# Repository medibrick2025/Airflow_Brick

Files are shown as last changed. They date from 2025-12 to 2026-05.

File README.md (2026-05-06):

# Airflow / Spiro Brick

The Spiro Brick interfaces with the [Sensirion SFM3300-D](https://sensirion.com/products/catalog/SFM3300-D) airflow sensor. It also enables airway pressure measurement using Amphenol differential pressure sensor such as [ELVH-family](https://allsensors.com/en/product-listing?family=elvh) with I2C 3.3V or 5V interface.

- [Datasheet SFM3300](./datasheets/Sensirion_Datasheet_SFM3300-AW_SFM3300-D.pdf)
- [Datasheet ELVH Family](./datasheets/DS-0376.pdf)

Example differential pressure sensor with I2C and 5V interface: ELVH-M160D-HRRD-C-N2A5 for 1/16 ID 1/8 OD tubing.

## Documentation

- [Education Background](./spirometer%20educational%20background/)
- [Assembly Instructions](./Spirometer%20Mechanical%20Design%20And%20Mechanical%20Assembly/)
- [Software / Firmware](./Spirometer%20Software/)

## SFM3300

- [Cleaning](./datasheets/Sensirion_GF_AN_SFM-21_Cleaning_Methods_D1.pdf)
- [Eval Kit](./datasheets/Sensirion_GF_AN_SFM-22_ClipOn_CapCable_Evaluation_Kit_D1_1.pdf)
- [Arduino Driver Sensirion](https://github.com/Sensirion/arduino-i2c-sfm3000) with [Sensirion Arduino Core](https://github.com/Sensirion/arduino-core)
- [Arduino Driver Alternative](https://github.com/MyElectrons/sfm3300-arduino)
 
## Spiro Brick PCB Design

The following files were created for this project using KiCad.

<a href="./KiCad/Altekreeti/Spiro_Brick.svg" target="_blank">
  Schematics
</a>

[View schematics as PDF](./KiCad/Altekreeti/Spiro_Brick.pdf)

<a href="./KiCad/Altekreeti/Spiro_Brick_Front.png" target="_blank"> 
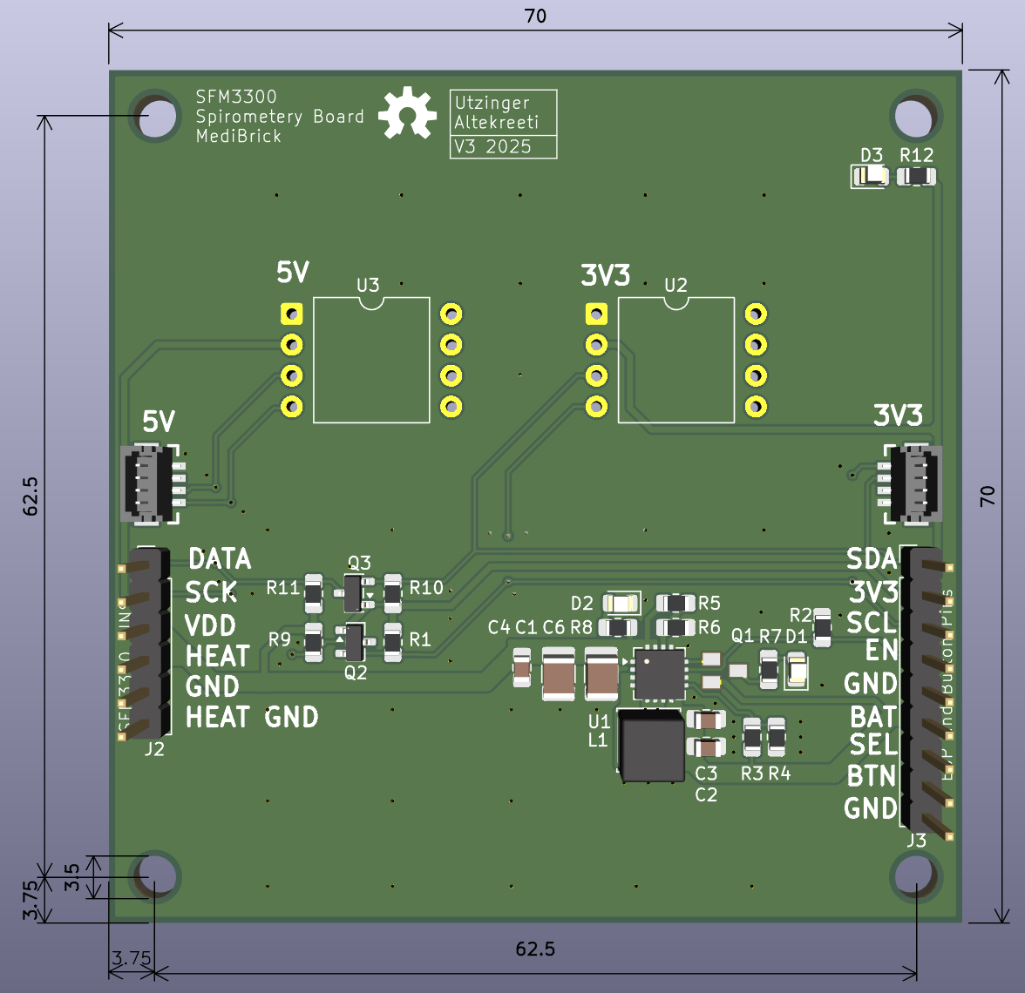
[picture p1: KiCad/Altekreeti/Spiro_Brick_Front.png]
  
</a>

<a href="./KiCad/Altekreeti/Spiro_Brick_Back.png" target="_blank">
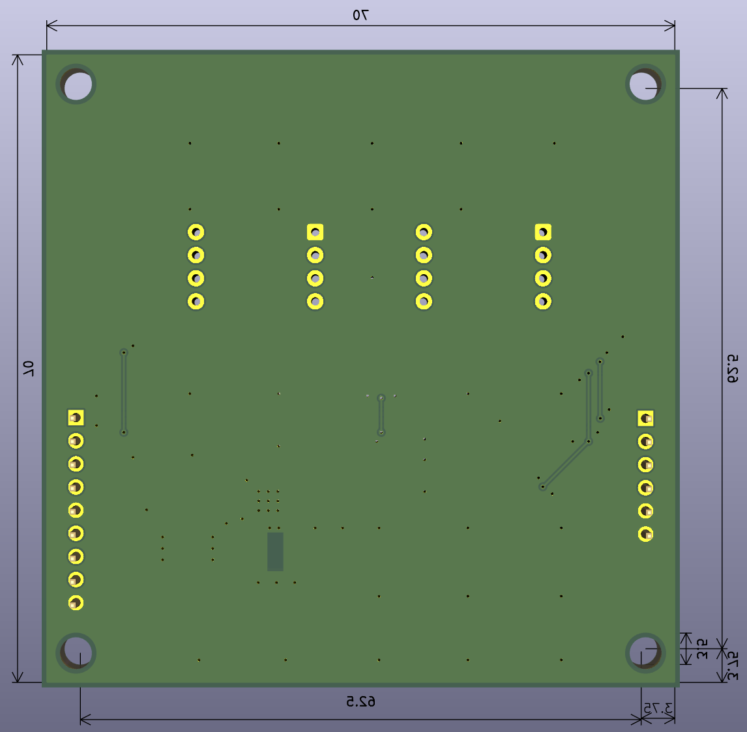
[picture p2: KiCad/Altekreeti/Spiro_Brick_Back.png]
  
</a>

## LiPo to 5V Power Boost

- [Ti TPS61090 Eval](./reference_designs/TPS61090_sbvu003.pdf)
- [Adafruit](https://learn.adafruit.com/adafruit-powerboost-500-plus-charger/downloads)

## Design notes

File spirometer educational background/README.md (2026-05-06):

**Introduction to Spirometry and Lung Volumes**

Spirometry is a fundamental respiratory test used to assess lung function by measuring the volume and flow of air during inhalation and exhalation. The test provides insights into a patient's breathing patterns and can be used to detect and monitor respiratory diseases. The Figure below shows the key lung volumes measures which includes:

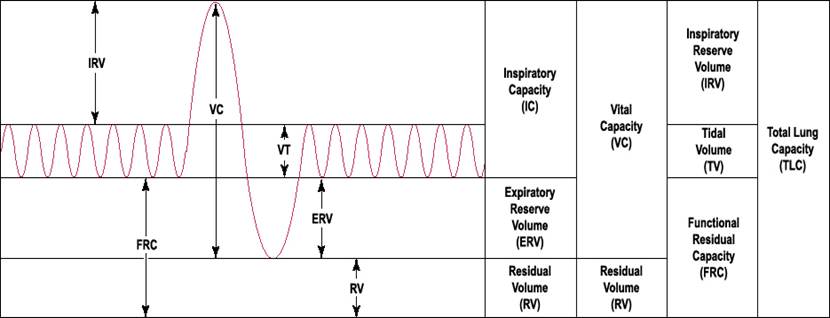
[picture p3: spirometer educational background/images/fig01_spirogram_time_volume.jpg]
Figure 1. Example spirogram showing lung volume as a function of time


[source](https://histology.oit.duke.edu/MBS/Videos/Phys/Phys%205.2%20Resp%20Lung%20Volumes/Phys%205.2%20Resp%20Lung%20Volumes.pdf)

- **Tidal Volume (TV):** The amount of air inhaled or exhaled during normal, resting breathing (typically 400–600 mL).
- **Inspiratory Reserve Volume (IRV):** Additional air that can be forcibly inhaled after a normal inhalation (~ above 1700 mL).
- **Expiratory Reserve Volume (ERV):** Additional air that can be forcibly exhaled after a normal exhalation (~800–1200 mL).
- **Residual Volume (RV):** Air remaining in the lungs after maximal exhalation (~1200 mL); not measurable by spirometry.
- **Inspiratory Capacity (IC):** Maximum air that can be inhaled after a normal exhalation; **IC = TV + IRV.**
- **Functional Residual Capacity (FRC):** Volume of air in lungs after a normal exhalation; **FRC = ERV + RV**.
- **Vital Capacity (VC):** Maximum amount of air that can be exhaled after a maximal inhalation; **VC = IRV + TV + ERV**.
- **Total Lung Capacity (TLC):** Total volume the lungs can hold; **TLC = VC + RV.**
- **Forced Vital Capacity (FVC):** The total amount of air exhaled during a forced breath (~3000–5000 mL).
- **FEV₁%:** The percentage of the FVC exhaled in the first second; this value helps assess obstruction ( +%90).
- **FEF₂₅–₇₅:** The average flow rate during the middle portion of a forced exhalation (4.5 L/s).

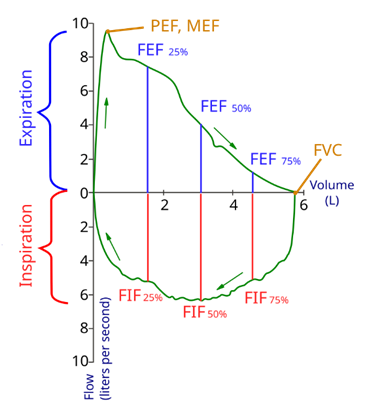
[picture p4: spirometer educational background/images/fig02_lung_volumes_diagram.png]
Figure 2. Lung volumes and capacities measured in spirometry


[source](https://en.wikipedia.org/wiki/Spirometry)

By plotting **flow versus volume**, a spirogram is generated, providing a visual representation of lung performance. This is especially useful for distinguishing between:

- **Normal lungs:** Full volume range, symmetrical loop.
- **Obstructive disorders (e.g., COPD):** Normal volume but reduced flow rate; scooped-out expiratory curves.
- **Restrictive disorders:** Reduced total lung volume with preserved flow patterns.

**Diagnose Normal Lung Function, Obstructive, or Restrictive Lung Disorder**

|     |     |     |     |
| --- | --- | --- | --- |
| Measured Value | Normal | Obstructive (Reduced Flow) | Restrictive (Reduced Capacity) |
| Lung Volumes (TV, IRV and ERV) | Normal: Equal or more than the expected volumes | Normal: About the expected volumes | Low: Significantly less than expected volumes |
| FVC | Normal | Normal | Low: Lungs move less than the normal amount of air |
| FEV₁% | Normal: 90%+ | Low: Less than ~70% of normal air flow | Normal: Airflow is normal |
| FEF₂₅–₇₅ | Normal: Equal or more than the normal value | Low: Significantly less than normal | Normal: Airflow is normal |

Case Analysis.

|     |     |     |     |
| --- | --- | --- | --- |
|     | TV (mL) | IRV (mL) | ERV (mL) |
| Case 1 | 400 | 2600 | 1000 |

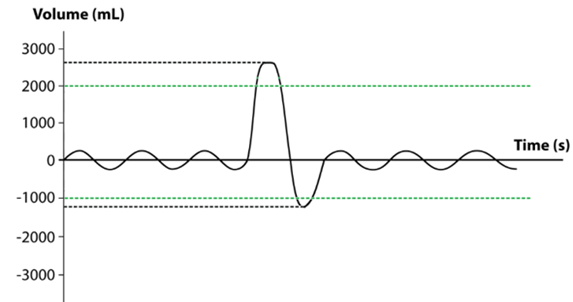
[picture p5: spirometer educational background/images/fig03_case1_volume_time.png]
Figure 3. Volume versus time curve for Case 1


|     |     |     |     |
| --- | --- | --- | --- |
|     | TV (mL) | IRV (mL) | ERV (mL) |
| Case 2 | 500 | 2300 | 900 |

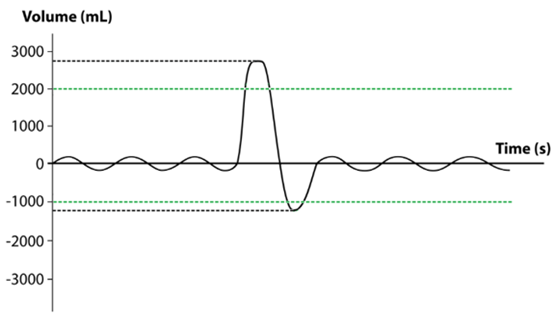
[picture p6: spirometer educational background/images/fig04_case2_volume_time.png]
Figure 4. Volume versus time curve for Case 2


|     |     |     |     |
| --- | --- | --- | --- |
|     | FVC (mL) | **FEV₁%** | **FEF₂₅–₇₅ (L/s)** |
| Case 1 | 4000 | 50  | 0.7 |

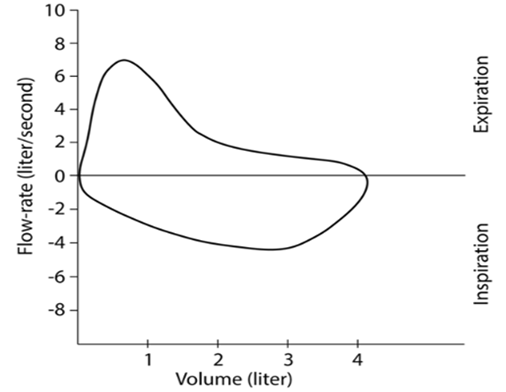
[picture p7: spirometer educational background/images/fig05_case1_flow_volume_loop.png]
Figure 5. Flow–volume loop for Case 1 indicating obstructive lung disease


|     |     |     |     |
| --- | --- | --- | --- |
|     | FVC (mL) | **FEV₁%** | **FEF₂₅–₇₅ (L/s)** |
| Case 2 | 3500 | 95  | 4.0 |

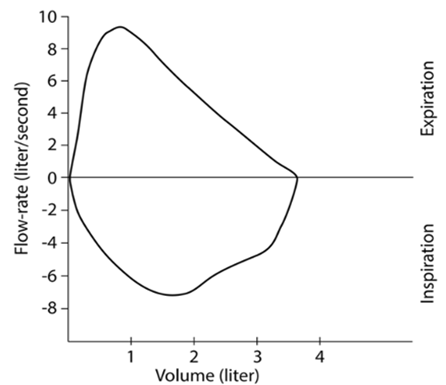
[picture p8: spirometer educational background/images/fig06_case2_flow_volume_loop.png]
Figure 6. Flow–volume loop for Case 2 showing normal lung function


- **Case 1** has normal FVC (4000 mL) but severely reduced FEV₁% (50%) and FEF₂₅–₇₅ (0.7 L/s), indicating **obstructive lung disease**, likely COPD.
- **Case 2** displays near-normal values (FVC 3500 mL, FEV₁% 95%, FEF₂₅–₇₅ 4.0 L/s), indicating **normal lung function**.

**Preface:**

The spirometer brick is a part of _MediBrick Project_. This spirometer device is designed specifically for educational demonstration and student experiments. The goal is to help learners understand the physics behind respiratory mechanics and thermal mass flow sensing, rather than to provide medical diagnostic results. By visualizing real-time flow data and calculated volume, students can connect theoretical principles with hands-on measurement.

**Composition of spirometer:**

The spirometer is mainly composed of these parts:

- Mouth piece
- airflow tube
- Flow sensor

( other electronics will be added later )

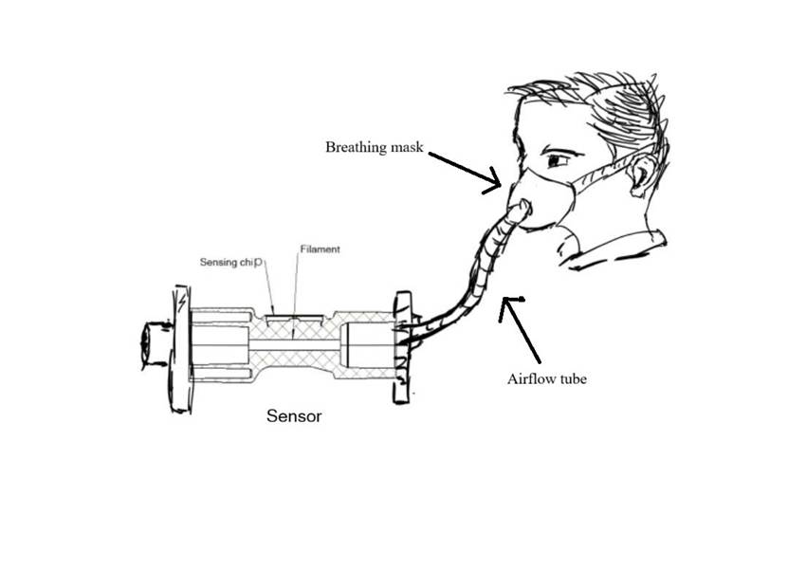
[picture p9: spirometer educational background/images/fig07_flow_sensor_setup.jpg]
Figure 7. Flow sensor setup showing airflow path from breathing mask to sensor


**Basic principle**

The flow sensor used in this project is SFM3300-D This is a thermal mass flow rate sensor that directly measures airflow. It has a bidirectional range (±250 slm) and outputs a digital flow value. Because it provides real-time flow data for both inhalation and exhalation, we do not require a separate differential pressure sensor to generate the spirogram (Flow vs Volume curve). This simplifies the design and enhances measurement accuracy for educational and demonstration purposes.

SFM3300-D uses Thermal Mass Flow Sensing technology.

Equation 1. Convective heat transfer relation

This equation is derived from the traditional theory of heat transfer and is the physical basis of the principle of thermal mass flow detection.

The working mechanism of SFM3300-D is based on this type of convective heat transfer and temperature difference detection. As the airflow passes through the sensor, it carries away the heat from the heating membrane, which calculates the mass flow rate by detecting changes in temperature difference, The heat-loss rate 

Q_dot definition

is proportional to the mass flow rate 

m_dot definition

:

Equation 2. Heat loss rate and mass flow relation

where 𝜌 is gas density, 𝐴 is the cross-sectional area, and 𝑣 is the average velocity.

Although the sensor measures rather than 𝑣, its digital output is converted to a standardized volume-flow rate 

Q_slm definition

under reference conditions:

Equation 3. Standardized volume flow definition

lung volumes are obtained by time integration:

Equation 4. Lung volume integration and velocity definition

Thus, the sensor’s flow-rate output effectively represents the average airflow speed inside the device.

In conventional airflow measurement, the gas density 𝜌 is assumed constant. However, in human exhalation, the molar mass 𝑀 and temperature 𝑇 both increase compared to ambient air, according to the ideal-gas law:

Equation 5. Ideal gas density relation

where 𝑅 is the universal gas constant and 𝑃 is pressure. Typical changes in 𝑀 (due to added CO₂ and H₂O) and in 𝑇 (warmer exhaled air) cause 𝜌 to vary by about 2–5 %. If the system assumes a fixed density when converting flow to volume, this produces a proportional error in the computed lung volume:

Equation 6. Volume error due to density variation

That means a 5 % density change would lead to roughly a 5 % volume-calculation error.

The SFM3300-D avoids this problem by directly measuring mass flow rather than velocity or volume flow. Because the measured variable already includes 

rho definition

. The sensor output inherently compensates for these density variations. Its on-chip digital temperature sensor further corrects for residual thermal effects, maintaining an accuracy of ±3 % of reading and only ±0.4 % per 10 °C temperature drift. These compensations are based on dry-air calibration. When measuring exhaled breath containing water vapor and CO₂, the gas properties slightly differ from the dry-air model, so an additional BTPS correction need to be applied in the spirometer software.

**Flow Measurement: Pressure Drop vs Thermal Sensing**

Traditionally, spirometers use a differential pressure sensor to measure the pressure drop across a resistance element and derive flow. However, the SFM3300-D sensor eliminates this need by providing direct mass flow measurement with high precision. Because it senses flow without relying on pressure differentials, there’s no need for multiple pressure ports or compensations.

By measuring mass flow directly, the SFM3300-D also inherently accounts for changes in gas density and temperature. This improves accuracy compared to simple velocity-based methods, especially when measuring exhaled air, which is warmer and contains more water vapor.

**Future Enhancements: Airway Pressure Monitoring**

Although a pressure sensor is not required for spirometry, adding one could expand the functionality of the device. For example, airway pressure monitoring is essential in applications like CPAP therapy, mechanical ventilation, and anesthesia machines. In these systems, pressure data is used to control airflow, protect the airway, and detect patient-triggered breathing efforts.

Sensirion’s evaluation kit for the SFM3300 series includes a clip-on module with a built-in pressure sensor, demonstrating how pressure sensing can be incorporated into a flow-based system. In future iterations, we may add such a sensor to study airway pressure dynamics alongside flow, further enriching the educational experience.

**Directions for use:**

( To be added, full components, Schematics, step by step Assembly instructions, Software/operation instructions / CAD models and electronics )

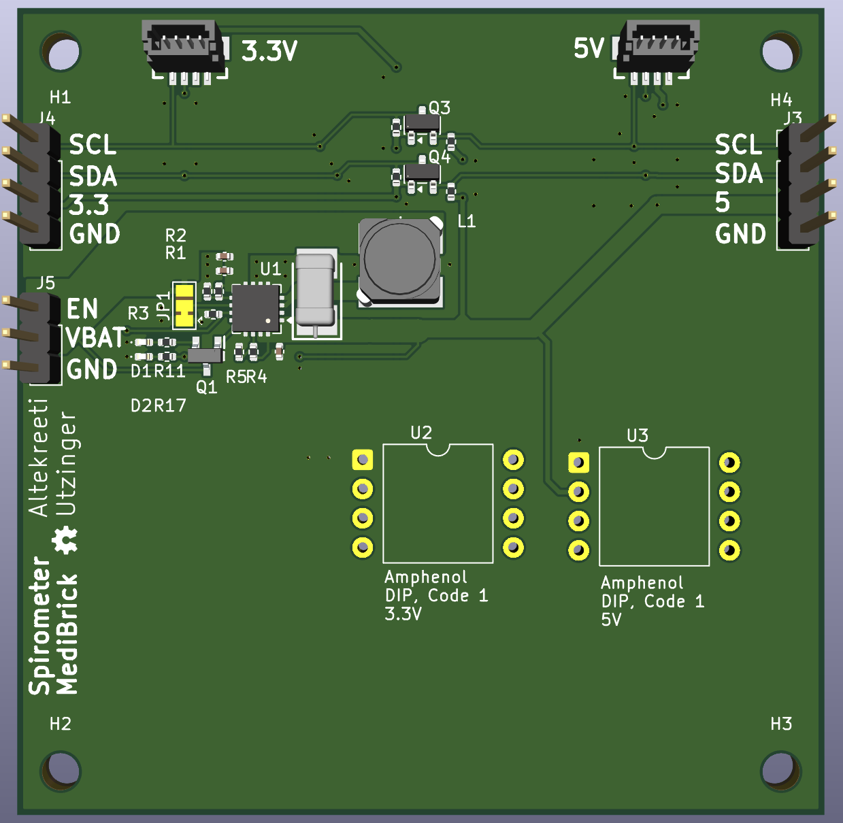
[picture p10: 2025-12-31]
KiCad/Utzinger/PCB.png

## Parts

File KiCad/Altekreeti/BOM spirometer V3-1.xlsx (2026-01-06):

Item # | Designator | Qty | Manufacturer | Mfg Part # | LCSC Part# | U.S. Distributor | Description / Value | Packaging | Type | Cost | Designation | Footprint | Remark
1 | Q2,Q3 | 2 | onsemi (https://www.lcsc.com/brand-detail/94.html) | BSS138 (https://www.lcsc.com/product-detail/C52895.html?s_z=n_BSS138) | C52895 (https://www.lcsc.com/product-detail/C52895.html?s_z=n_BSS138) |  | N-Channel 50V 0.22A 0.36W Surface Mount SOT-23 | SOT-23 | SMD | $0.06 | BSS138 | SOT-23
2 | C1,C6 | 2 | YAGEO (https://www.lcsc.com/brand-detail/396.html) | CC1210MKX5R6BB107 (https://www.lcsc.com/product-detail/C723734.html) | C723734 (https://www.lcsc.com/product-detail/C723734.html) |  | 100uF ±20% 10V Ceramic Capacitor X5R 1210 | 1210 | SMD | $0.68 | 100uF | C_1210_3225Metric_Pad1.33x2.70mm
3 | R7,R8,R12 | 2 | YAGEO (https://www.lcsc.com/brand-detail/396.html) | RC0805FR-071KL (https://www.lcsc.com/product-detail/C95781.html?s_z=n_RC0805FR-071KL) | C95781 (https://www.lcsc.com/product-detail/C95781.html?s_z=n_RC0805FR-071KL) |  | RES 1kΩ ±1% 125mW 0805 | 805 | SMD | $0.002 | 1K | R_0805_2012Metric_Pad1.20x1.40mm
4 | L1 | 1 | cjiang (https://www.lcsc.com/brand-detail/11425.html) | FNR5040S6R8MT (https://www.lcsc.com/product-detail/C167965.html?s_z=n_YAGEO%25206.8Uh) | C167965 (https://www.lcsc.com/product-detail/C167965.html?s_z=n_YAGEO%25206.8Uh) |  | 6.8uH Magnetic Shielded Inductor 3.4A SMD,5x5mm Fixed Inductors RoHS | 5x5mm | SMD | $0.093 | 6.8uH | L_Changjiang_FNR5045S
5 | C4 | 1 | YAGEO (https://www.lcsc.com/brand-detail/396.html) | CC0805KKX5R8BB225 (https://www.lcsc.com/product-detail/C277526.html) | C277526 (https://www.lcsc.com/product-detail/C277526.html) |  | 2.2uF ±10% 25V Ceramic Capacitor X5R 0805 | 805 | SMD | $0.0184 | 2.2uF | C_0805_2012Metric_Pad1.18x1.45mm
6 | D2 | 1 | XINGLIGHT (https://www.lcsc.com/brand-detail/12469.html) | XL-2012UGC (https://www.lcsc.com/product-detail/C965815.html?s_z=n_LED_0805_2012Metric_GREEN_COLOR) | C965815 (https://www.lcsc.com/product-detail/C965815.html?s_z=n_LED_0805_2012Metric_GREEN_COLOR) |  | Green LED | 805 | SMD | $0.0057 | GRN | LED_0805_2012Metric_GREEN_COLOR
7 | R4 | 1 | YAGEO | RC0805FR-07340KL (https://www.lcsc.com/product-detail/C137543.html?s_z=n_YAGEO%2520RC0805FR-07340KL) | C137543 (https://www.lcsc.com/product-detail/C137543.html?s_z=n_YAGEO%2520RC0805FR-07340KL) |  | RES 340kΩ ±1% 125mW | 805 | SMD | $0.0021 | 340K | R_0805_2012Metric_Pad1.20x1.40mm
8 | R2 | 1 | YAGEO (https://www.lcsc.com/brand-detail/396.html) | RC0805FR-07100KL (https://www.lcsc.com/product-detail/C96346.html?s_z=n_RC0805FR-07100KL) | C96346 (https://www.lcsc.com/product-detail/C96346.html?s_z=n_RC0805FR-07100KL) |  | RES 100kΩ ±1% 125mW 0805 | 805 | SMD | $0.0025 | 100k | R_0805_2012Metric_Pad1.20x1.40mm
9 | C3 | 1 | Samsung Electro-Mechanics (https://www.lcsc.com/brand-detail/254.html) | CL21A106KBYQNNE (https://www.lcsc.com/product-detail/C2932476.html) | C2932476 (https://www.lcsc.com/product-detail/C2932476.html) |  | 10uF ±10% 50V Ceramic Capacitor X5R 0805 | 805 | SMD | $0.0414 | 10uF | C_0805_2012Metric_Pad1.18x1.45mm
10 | R5 | 1 | Walsin (https://www.lcsc.com/brand-detail/450.html) | WR08W1804FTL (https://www.lcsc.com/product-detail/C170816.html?s_z=n_%2520C170816) | C170816 (https://www.lcsc.com/product-detail/C170816.html?s_z=n_%2520C170816) |  | RES 1.8MΩ ±1% 125mW 0805 | 805 | SMD | $0.0054 | 1.80M | R_0805_2012Metric_Pad1.20x1.40mm
11 | Q1 | 1 | onsemi (https://www.lcsc.com/brand-detail/94.html) | MMUN2133LT1G (https://www.lcsc.com/product-detail/C86182.html?s_z=n_MMUN2133LT1G) | C86182 (https://www.lcsc.com/product-detail/C86182.html?s_z=n_MMUN2133LT1G) |  | Pre-Biased Bipolar Transistor (BJT) 50V 100mA 246mW Surface Mount SOT-23 | SOT-23 | SMD | $0.0306 | MMUN2133LT1G | SOT95P240X111-3N
12 | R11,R9,R1,R10 | 4 | YAGEO (https://www.lcsc.com/brand-detail/396.html) | RC0805FR-0710KL (https://www.lcsc.com/product-detail/C84376.html?s_z=n_RC0805FR-0710KL) | C84376 (https://www.lcsc.com/product-detail/C84376.html?s_z=n_RC0805FR-0710KL) |  | RES 10kΩ ±1% 125mW | 805 | SMD | $0.0019 | 10K | R_0805_2012Metric_Pad1.20x1.40mm
13 | R3 | 1 | Walsin (https://www.lcsc.com/brand-detail/450.html) | WR08W1874FTL (https://www.lcsc.com/product-detail/C367830.html?s_z=n_%2520C367830) | C367830 (https://www.lcsc.com/product-detail/C367830.html?s_z=n_%2520C367830) |  | RES 1.87MΩ ±1% 125mW 0805 | 805 | SMD | $0.0053 | 1.87M | R_0805_2012Metric_Pad1.20x1.40mm
14 | U1 | 1 | TI | TPS61030RSAR (https://www.lcsc.com/product-detail/C10110.html?s_z=n_TI%2520TPS61030) | C10110 (https://www.lcsc.com/product-detail/C10110.html?s_z=n_TI%2520TPS61030) |  | 600kHz Boost Adjustable 1.8V~5.5V 1A QFN-16-EP(4x4) Voltage Regulators - DC DC Switching Regulators RoHS | QFN-16-EP(4x4) | SMD | $1.6899 | TPS61090 | Texas_RSA_VQFN-16-1EP_4x4mm_P0.65mm_EP2.7x2.7mm_ThermalVias
15 | D1 | 1 | XINGLIGHT (https://www.lcsc.com/brand-detail/12469.html) | XL-2012SURC (https://www.lcsc.com/product-detail/C965812.html) | C965812 (https://www.lcsc.com/product-detail/C965812.html) |  | RED LED | 805 | SMD | $0.0059 | RED LED | LED_0805_2012Metric_RED_COLOR
16 | R6 | 1 | YAGEO (https://www.lcsc.com/brand-detail/396.html) | RT0805BRD07200KL (https://www.lcsc.com/product-detail/C728645.html?s_z=n_RT0805BRD07200KL) | C728645 (https://www.lcsc.com/product-detail/C728645.html?s_z=n_RT0805BRD07200KL) |  | RES 200kΩ ±0.1% 125mW 0805 | 805 | SMD | $0.0336 | 200K | R_0805_2012Metric_Pad1.20x1.40mm
17 | C2 | 1 | YAGEO (https://www.lcsc.com/brand-detail/396.html) | CC0805KRX7R8BB104 (https://www.lcsc.com/product-detail/C519981.html?s_z=n_CC0805KRX5R8BB104) | C519981 (https://www.lcsc.com/product-detail/C519981.html?s_z=n_CC0805KRX5R8BB104) |  | 100nF ±10% 25V Ceramic Capacitor X7R 0805 | 805 | SMD | $0.0059 | 100nF | C_0805_2012Metric_Pad1.18x1.45mm
18 | D3 | 1 | XINGLIGHT (https://www.lcsc.com/brand-detail/12469.html) | XL-2012UBC (https://www.lcsc.com/product-detail/C965817.html?s_z=n_C965817) | C965817 (https://www.lcsc.com/product-detail/C965817.html?s_z=n_C965817) |  | Blue LED | 805 | SMD | $0.0064 | BLUE LED | LED_0805_2012Metric
19 | J1,J4 | 2 | JST (https://www.lcsc.com/brand-detail/853.html) | BM04B-SRSS-TBT(LF)(SN) (https://www.lcsc.com/product-detail/C495539.html?s_z=n_BM04B-SRSS-TBT) | C495539 (https://www.lcsc.com/product-detail/C495539.html?s_z=n_BM04B-SRSS-TBT) |  | Connector Header 4 position 1mm Pitch 1A Surface Mount,Vertical -25℃~+85℃ | SMD,P=1mm | SMD | $0.3124 | JST_I2C | JST_SMD_1.0mm_Vertical
20 | J3 | 1 |  |  |  |  | Do not Place |  |  |  | Conn_01x09_Pin | PinHeader_1x09_P2.54mm_Vertical | Do not Place
21 | J2 | 1 |  |  |  |  | Do not Place |  |  |  | ~ | PinHeader_1x06_P2.54mm_Vertical | Do not Place

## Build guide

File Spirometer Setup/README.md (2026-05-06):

## 6.0 Assembly and Use Instructions

### 6.1 Spirometer

#### 6.1.1 Electrical Assembly

##### Soldering

###### SFM3300 Flow Sensor Connection (SFM headers)

The left-side header of the Spirometer MediBrick is dedicated to the SFM3300 airflow sensor interface.

Firmly insert wires or a pin header into the pads labeled **DATA**, **SCK**, **VDD**, **HEAT**, and **GND**.  
These pads are directly connected to the corresponding SFM3300 sensor pins.

Solder each connection securely, ensuring correct alignment and solid solder joints for reliable airflow measurement and heater control.

###### Microcontroller Interface (Right Side Header)

The right-side header is used to connect the Spirometer MediBrick to the Adafruit Feather ESP32-S3 microcontroller.

Insert wires or a header into the pads labeled **SDA**, **SCL**, **3V3**, **GND**, **EN**, **BAT**, **SEL**, **BTN**, and **GND**.  
Solder all required pins carefully, avoiding solder bridges between adjacent pads.

##### Wires

Attach color-coded wires to the I/O pads as follows:

- **Red**: Power (3V3)  
- **Black or Green**: Ground (GND)  
- **Blue or White**: I²C signals (SDA, SCL)  
- **Other colors**: Control signals (EN, BTN)

Wires may be inserted directly into the through-holes (perpendicular) or attached as short pigtail leads soldered onto the pads.

##### Suggested Connections to the Adafruit Feather ESP32-S3

The recommended connections between the Spirometer MediBrick and the ESP32-S3 are shown below:

| PCB | ESP |
|-----|-----|
| SDA | SDA |
| 3V3 | 3.3 |
| SCL | SCL |
| EN  | A5  |
| GND | GND |
| BAT | VBAT |
| SEL | GPIO 9 |
| BTN | Button |
| GND | Button |

<a href="./images/image01.jpeg" target="_blank">
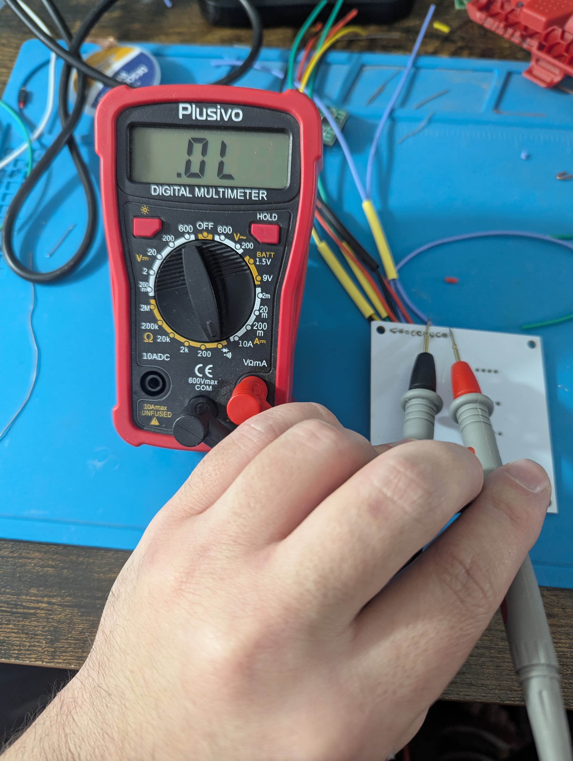
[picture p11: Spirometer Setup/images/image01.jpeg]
Spirometer setup photo 1
  
</a>

<a href="./images/image02.jpeg" target="_blank">
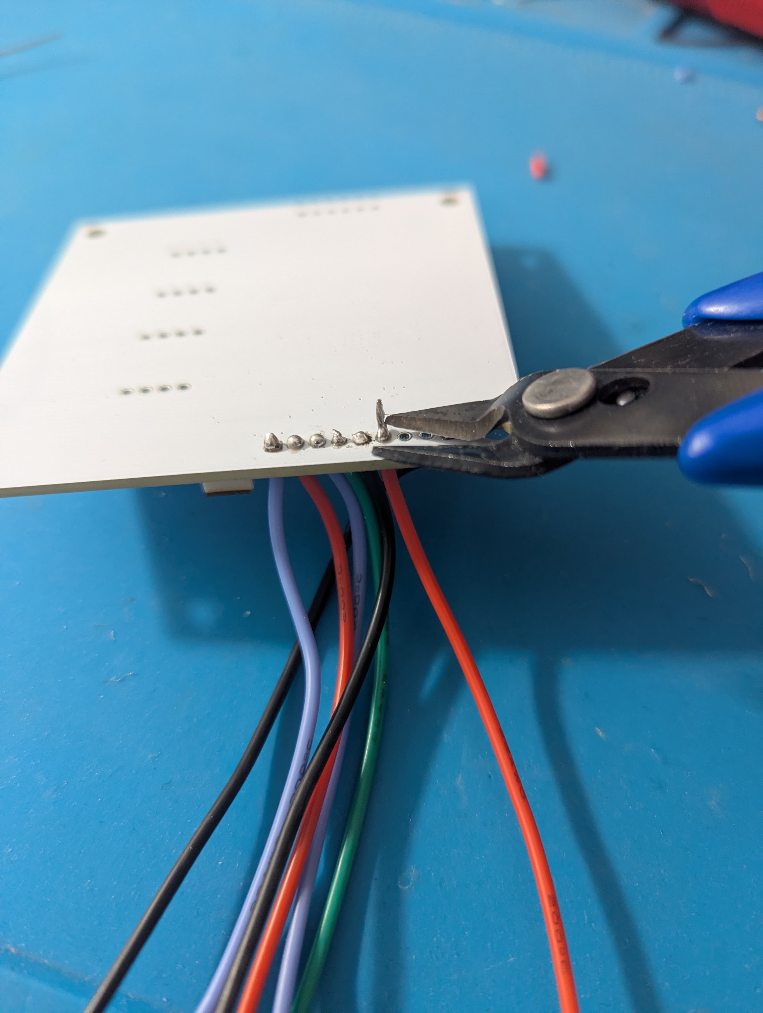
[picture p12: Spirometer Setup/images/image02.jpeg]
Spirometer setup photo 2
  
</a>

<a href="./images/image03.jpeg" target="_blank">
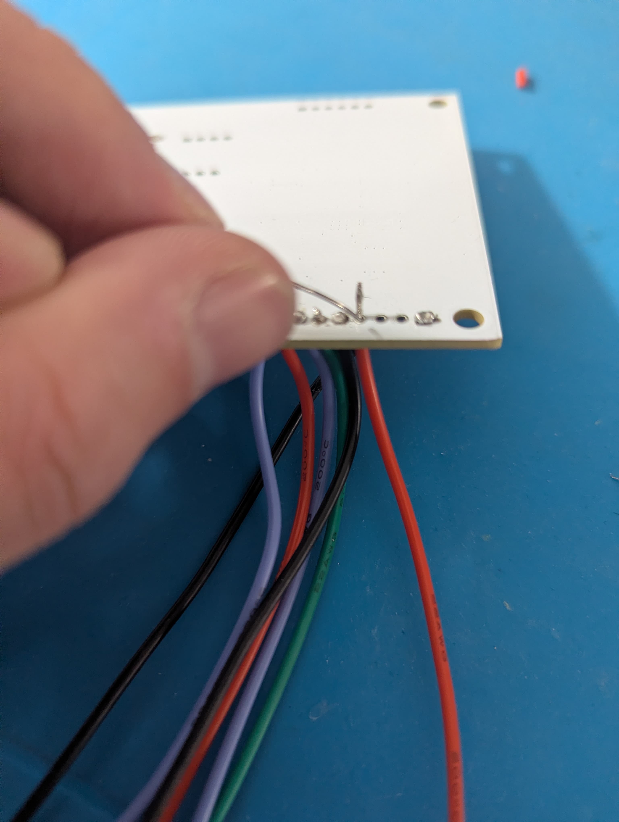
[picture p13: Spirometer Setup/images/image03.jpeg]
Spirometer setup photo 3
  
</a>

<a href="./images/image04.jpeg" target="_blank">
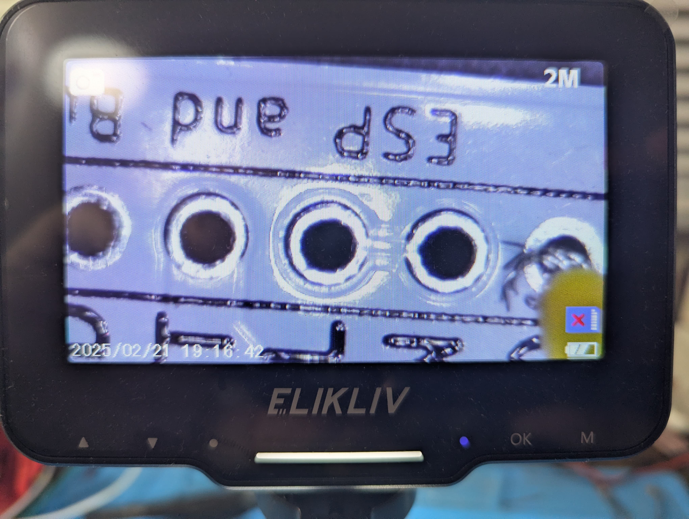
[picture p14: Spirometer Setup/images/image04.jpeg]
Spirometer setup photo 4
  
</a>

<a href="./images/image05.jpeg" target="_blank">
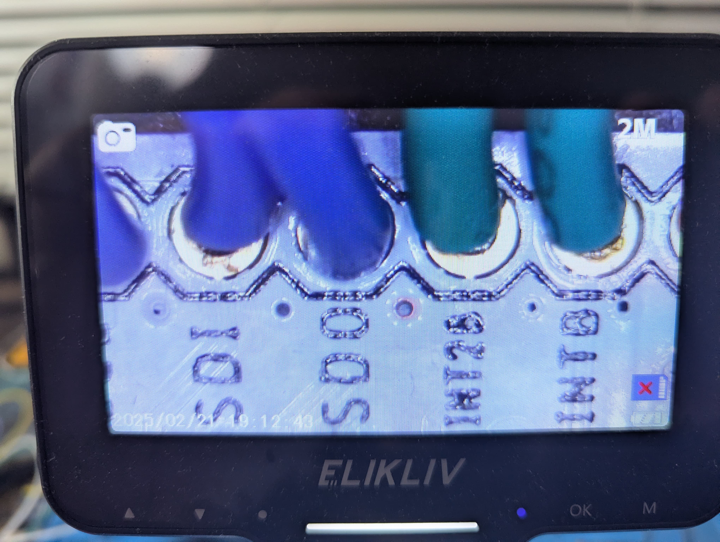
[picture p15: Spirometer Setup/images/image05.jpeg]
Spirometer setup photo 5
  
</a>

##### Final Inspection

After assembly:

- Verify all solder joints are clean and fully wetted.
- Confirm correct wiring orientation for the SFM3300 sensor.
- Check continuity for power and ground connections using a multimeter.
- Ensure no short circuits exist between adjacent pins.
- Run an I²C check.
- Run the test code.

Once completed, the Spirometer MediBrick is ready for enclosure integration and functional testing with the ESP32-S3.

##User manual

Before powering on the device
The Spirometer MediBrick needs 3.7V from the battery to properly power the complete system. Make sure before the device is ran that the battery is correctly attached to its input on the microcontroller.  

## Battery Connection

<p align="center">
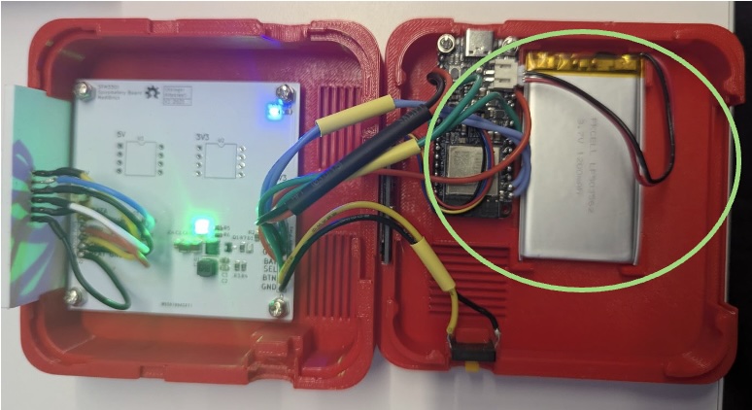
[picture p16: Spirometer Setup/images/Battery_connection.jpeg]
Battery Connection
  
</p>

Burning the code
To start collecting data from the Spirometer MediBrick, the most important step is to make sure that the code is properly uploaded to the system. This can be done by attaching the computer to the Spirometer device. Once connected, the code provided on the MediBrick GitHub page should be uploaded to Arduino IDE and uploaded onto the microcontroller. The display should show your inhale and exhale volumes around 0 if properly done.

Reading the Data
The display on the device shows the inhalation and exhalation volumes when in use and holds any readings if not. After use, the device will show the maximum achieved inhalation or exhalation volume.
Resetting Instructions
If an error occurs within the code itself, disconnect the spirometer sensor and re attach it. After the display powers back on, click the reset button found on the side of the device twice to fully reset the sensor. This will allow normal readings and measurements to be gathered

## Deep Sleep

<p align="center">
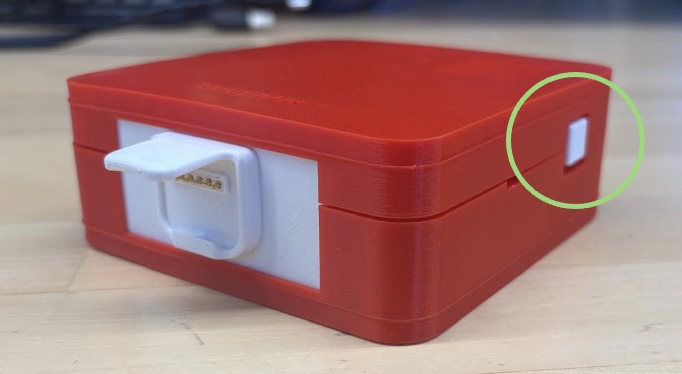
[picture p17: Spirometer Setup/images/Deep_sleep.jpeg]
Deep Sleep
  
</p>

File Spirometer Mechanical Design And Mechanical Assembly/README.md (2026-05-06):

# Spirometer Mechanical Design

This folder contains the mechanical design files for the Spirometer Brick enclosure.

# Components needed:

3D printing of
•	[Faceplate OnShape-](https://cad.onshape.com/documents/8a012de4c38b63333db6af02/w/265b6d782bd2385b1745b6bb/e/89639c93393428ddd956de37)
Purchasing of
•	[Pogo-Pins-](https://www.digikey.com/en/products/detail/mill-max-manufacturing-corp/0929-0-15-20-75-14-11-0/1873763)

#Instructions:
1. Gather all of the materials requested as well as solder, heat shrinks, and the soldering iron from the Salter Lab.
2. Follow the electrical assembly instructions for the spirometer listed on the GitHub, this should leave one with an ESP with 6 unsoldered wires that will be attached to the faceplate.
3. Tape a section above the back of the faceplate and label it as so:

## Faceplate Pinout

<p align="center">
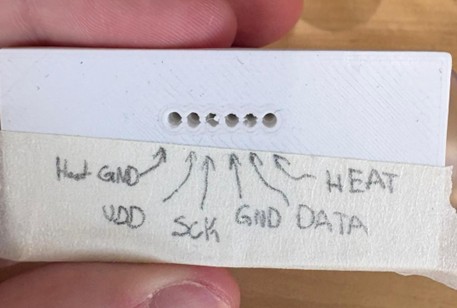
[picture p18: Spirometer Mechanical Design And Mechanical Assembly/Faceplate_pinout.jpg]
Faceplate Pinout
  
</p>

This will reduce any confusion of where to solder each wire from the ESP to the pogo pins.  As the wiring to the sensor must be accurate with the datasheet design found below:

## Sensor Pinout

<p align="center">
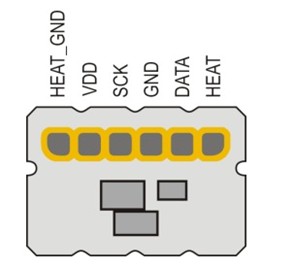
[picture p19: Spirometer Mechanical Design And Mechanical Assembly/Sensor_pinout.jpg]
Sensor Pinout
  
</p>

4. Pass heat shrink onto all 6 wires that will be soldered onto the pogo pins. This prepares the heat shrink for step 6
5. Solder the wires onto the pogo pins. The instructions for which pin attaches to which wire is listed on the spirometer electrical assembly. It is helpful to space each wire out so the chance of pins shorting or soldering to each other is avoided.
6. Pull the previously placed heat shrink over the soldered portion. Do not heat the heat shrink to set it at this stage
7. Push the pins into the holes of the spirometer faceplate. Make sure that the pins go into the faceplate as far as possible, and all of the spring-loaded portion of the pogo pin is visible on the connector face. This can be done by taking a flat tool like a screwdriver and pushing the pin until its bottom is flush with the faceplate.
8. After adjusting the heat shrink as needed such that it sufficiently covers the backside of the pins and the soldered portion, heat them with a heat gun to set them. Visually inspect to make sure there are no accidental shorts between the pins. The heat shrink should provide an extra layer of insulation to protect from short circuits.

## Designer
Mechanical design provided by Shafayet.

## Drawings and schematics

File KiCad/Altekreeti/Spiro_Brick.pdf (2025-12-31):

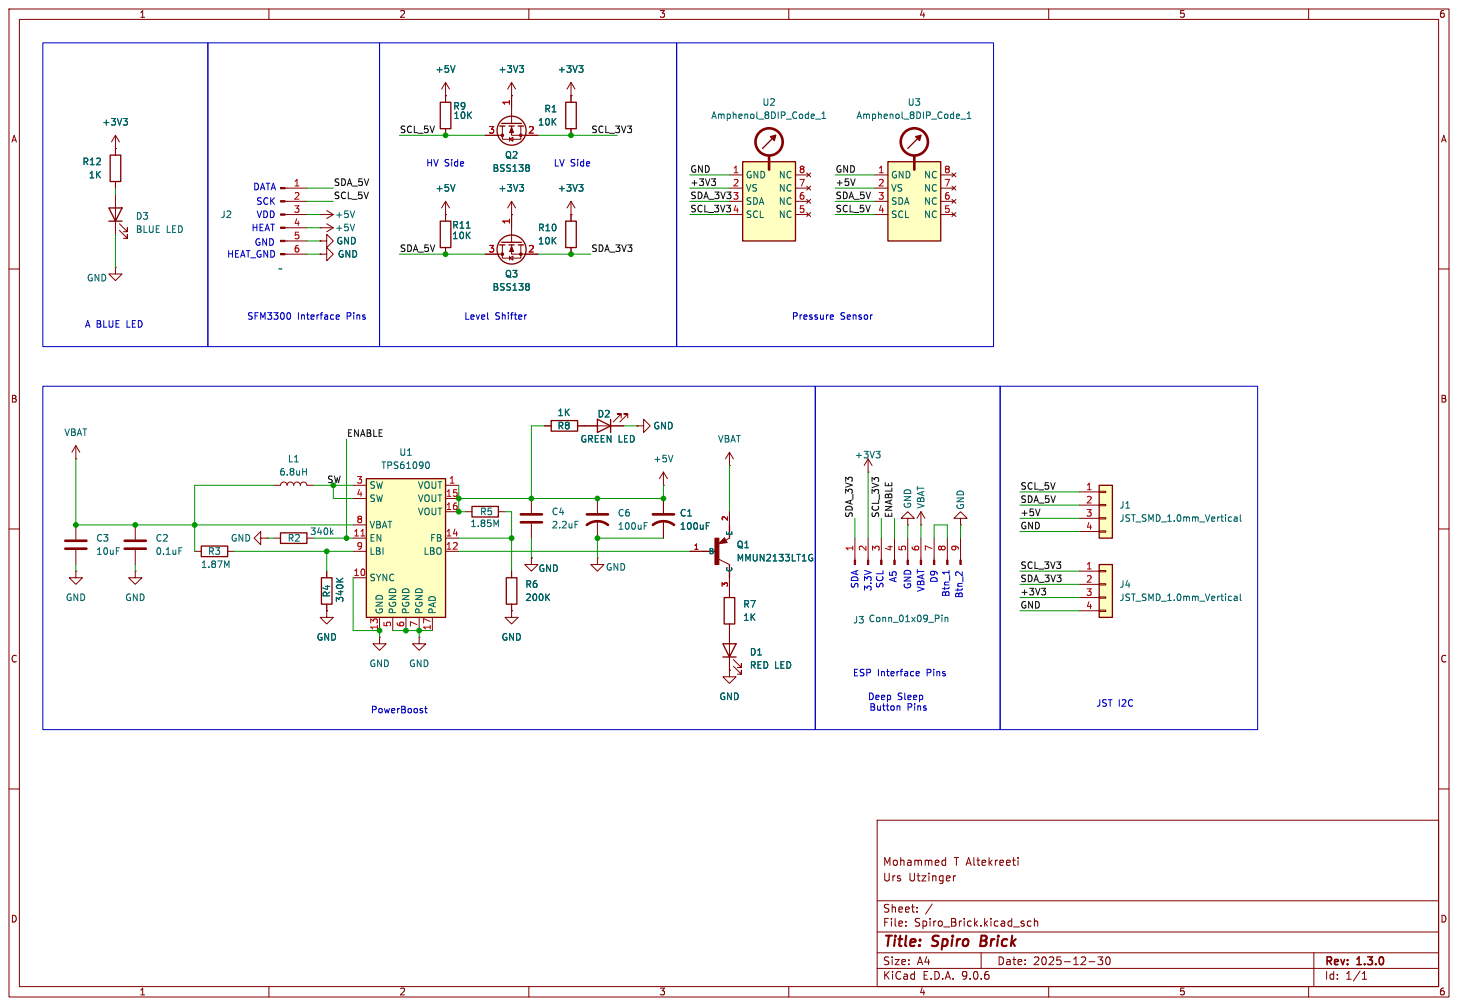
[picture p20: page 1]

Level Shifter HEAT VDD

7 PAD 17 VOUT 1 VOUT 15 VOUT 16 FB 14

Id: 1/1 Title: Spiro Brick

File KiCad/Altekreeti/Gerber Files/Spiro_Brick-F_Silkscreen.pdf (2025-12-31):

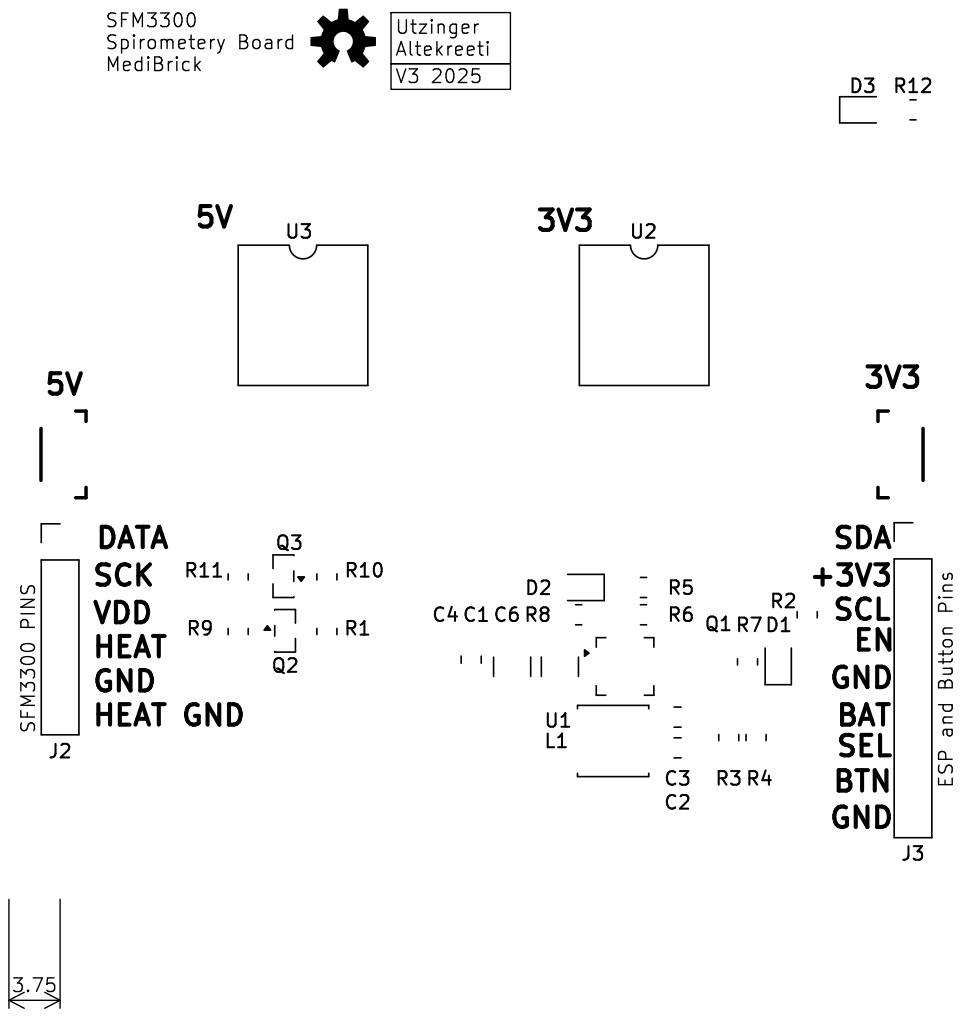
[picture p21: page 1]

Utzinger Altekreeti HEAT GND

Id: 5/11 Title: Spiro Brick

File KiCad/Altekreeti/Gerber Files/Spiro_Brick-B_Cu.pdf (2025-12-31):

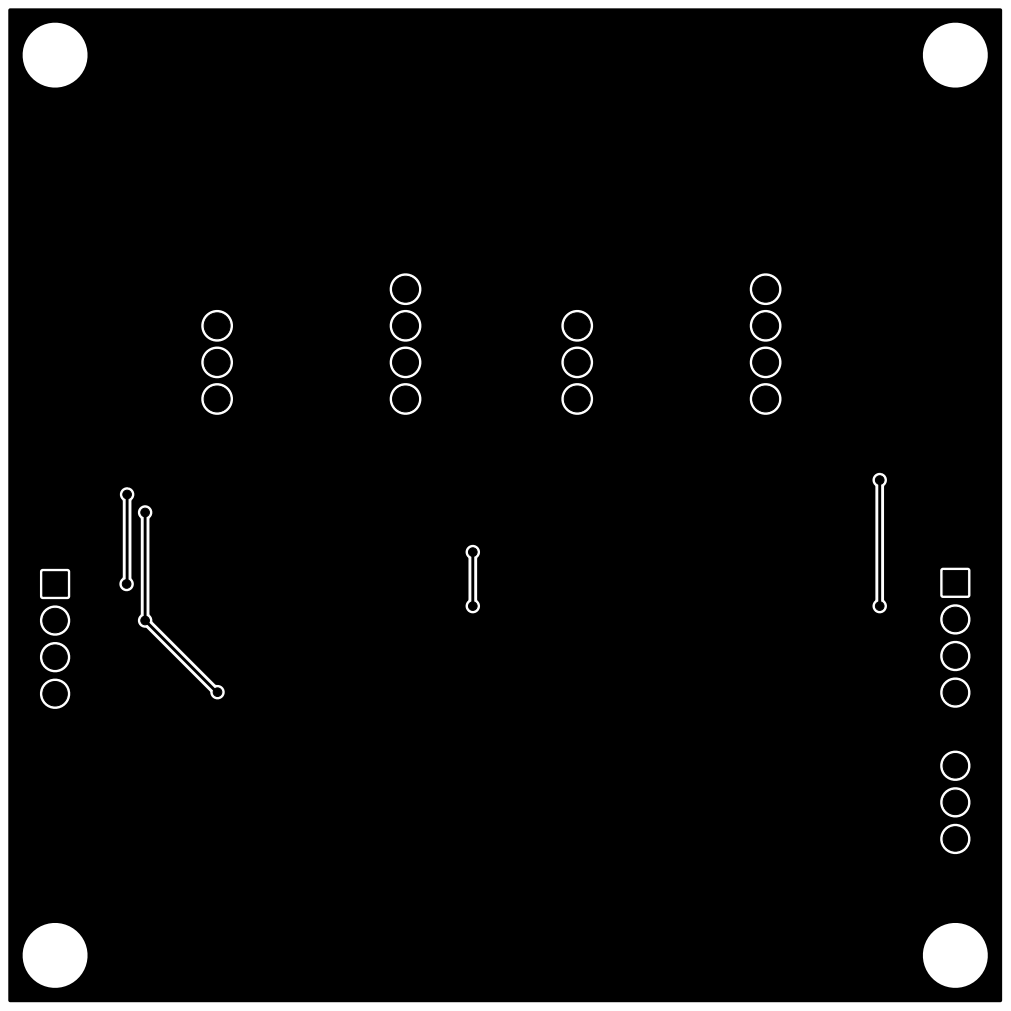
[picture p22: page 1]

Id: 2/11 Title: Spiro Brick

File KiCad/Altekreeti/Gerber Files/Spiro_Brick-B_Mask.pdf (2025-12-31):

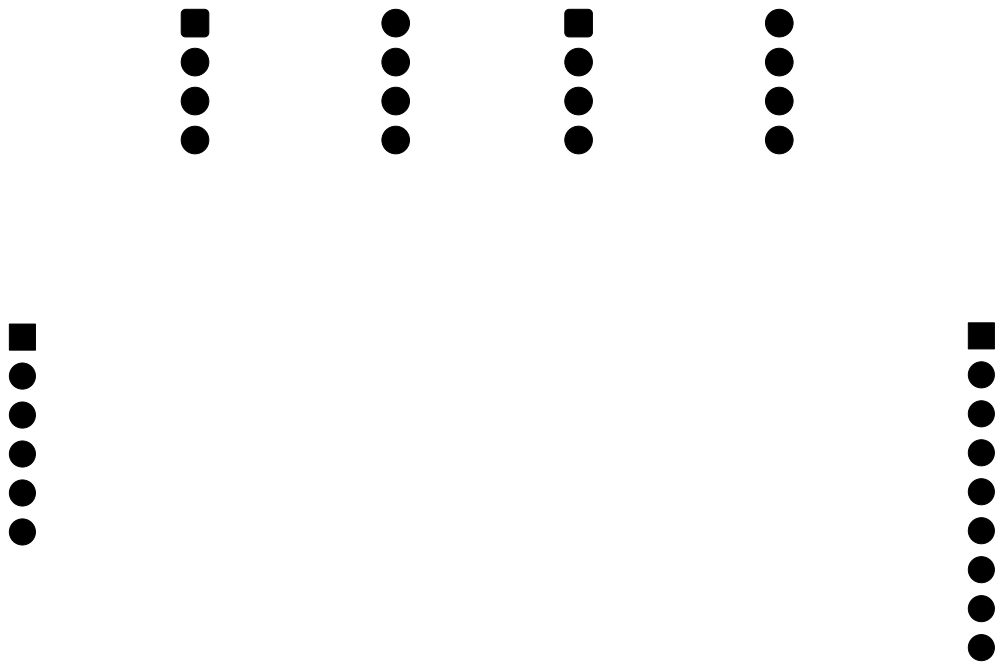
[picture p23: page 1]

Id: 8/11 Title: Spiro Brick

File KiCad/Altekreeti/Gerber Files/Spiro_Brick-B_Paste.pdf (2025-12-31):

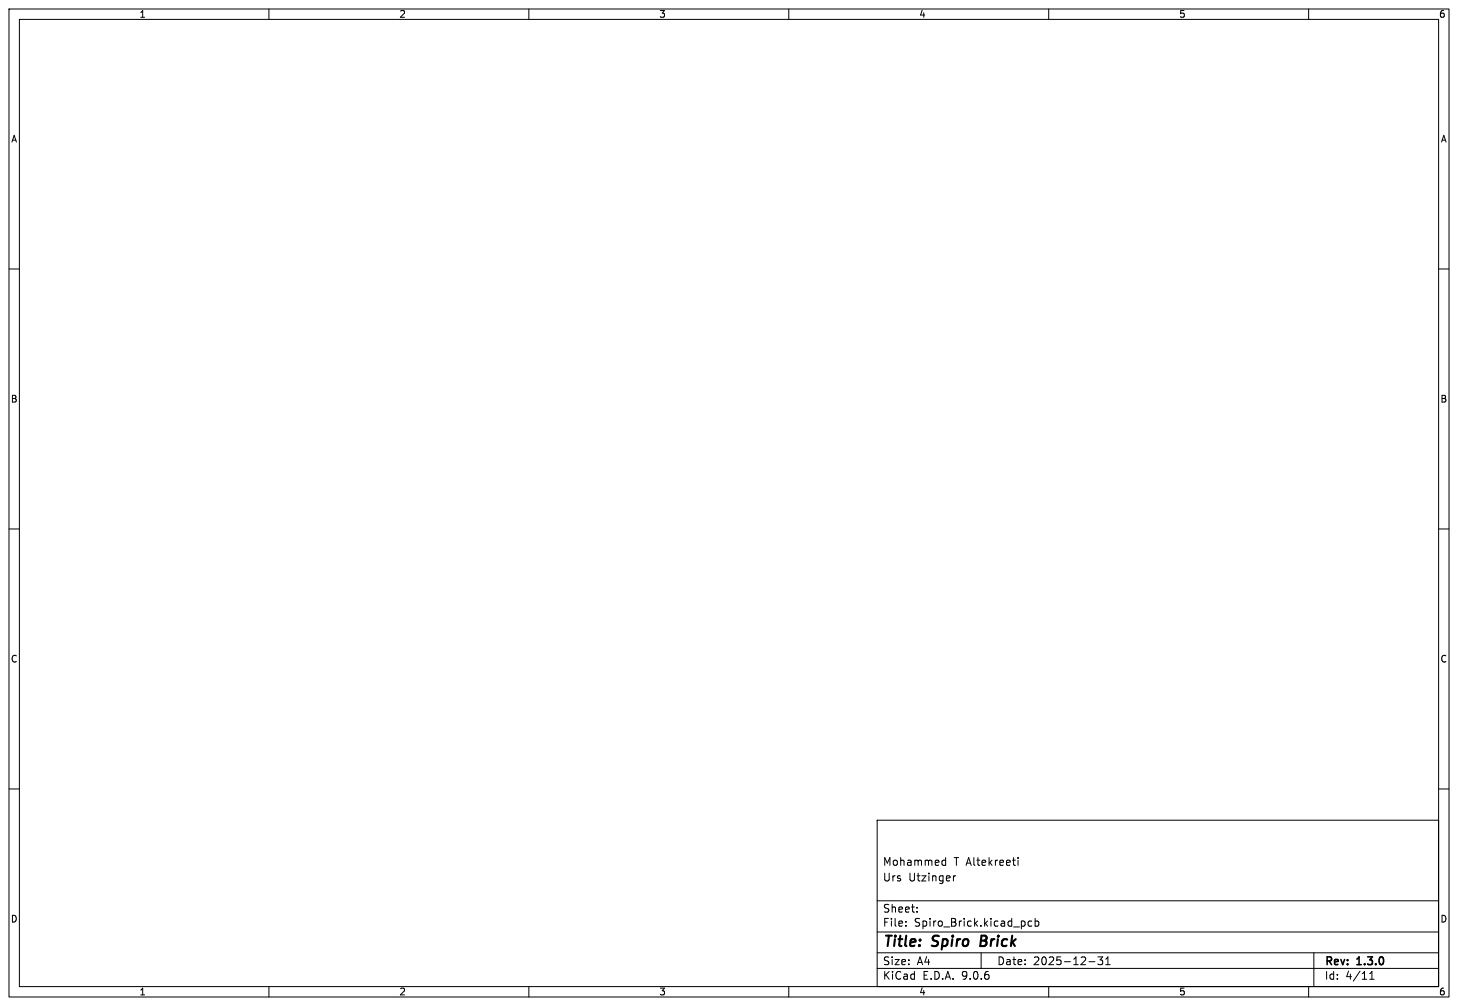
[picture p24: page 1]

Id: 4/11 Title: Spiro Brick

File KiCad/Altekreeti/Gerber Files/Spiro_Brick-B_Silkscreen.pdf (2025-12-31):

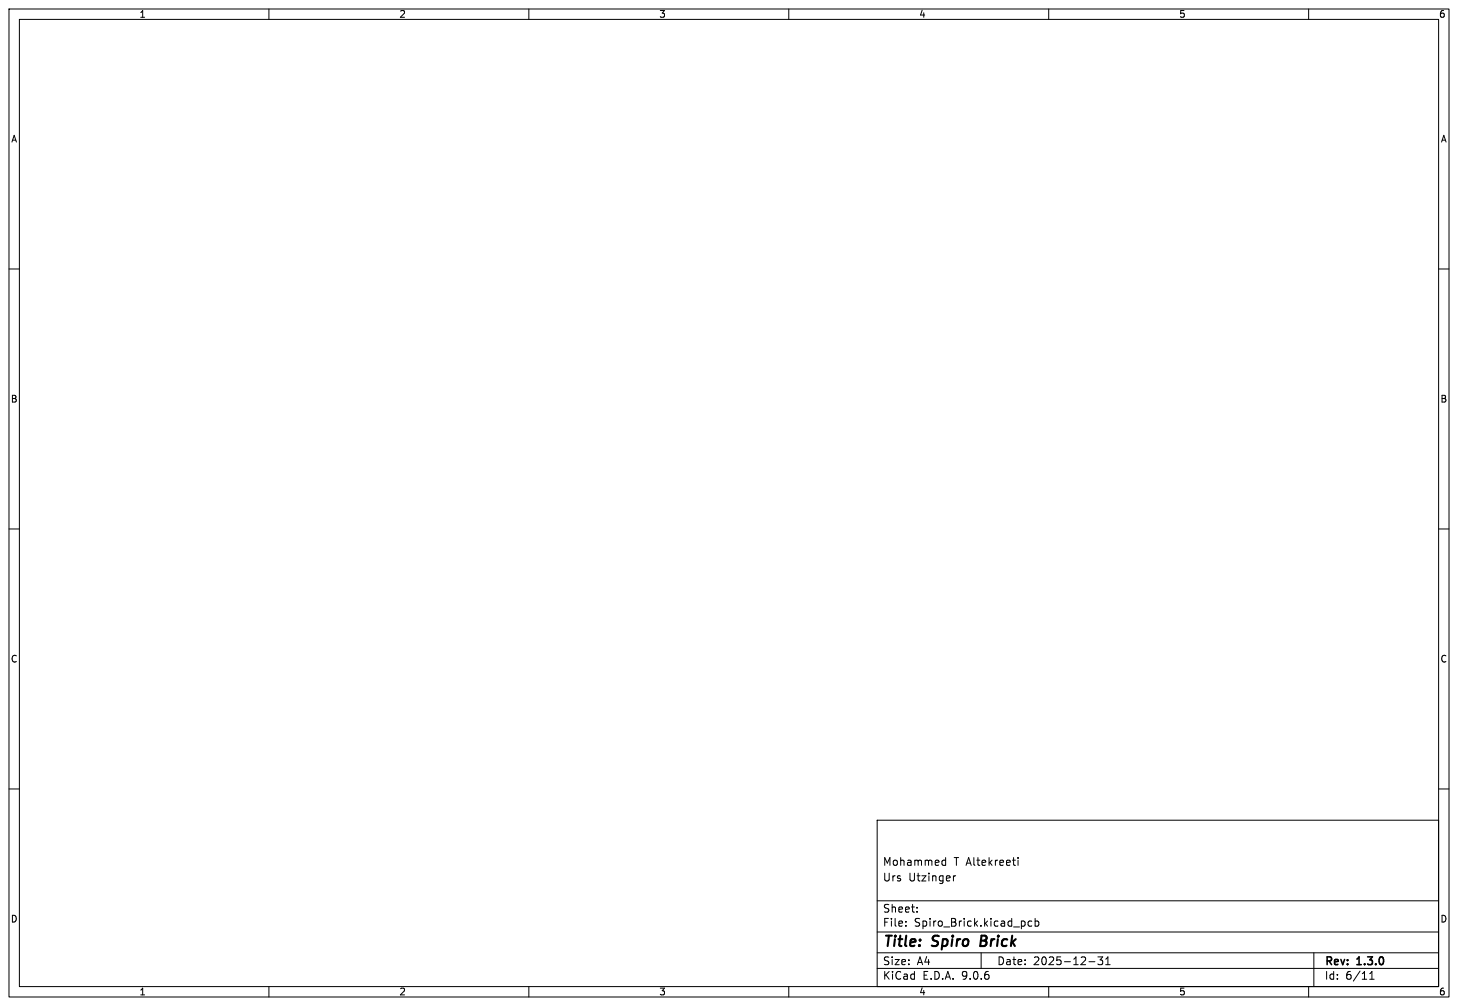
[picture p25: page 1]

Id: 6/11 Title: Spiro Brick

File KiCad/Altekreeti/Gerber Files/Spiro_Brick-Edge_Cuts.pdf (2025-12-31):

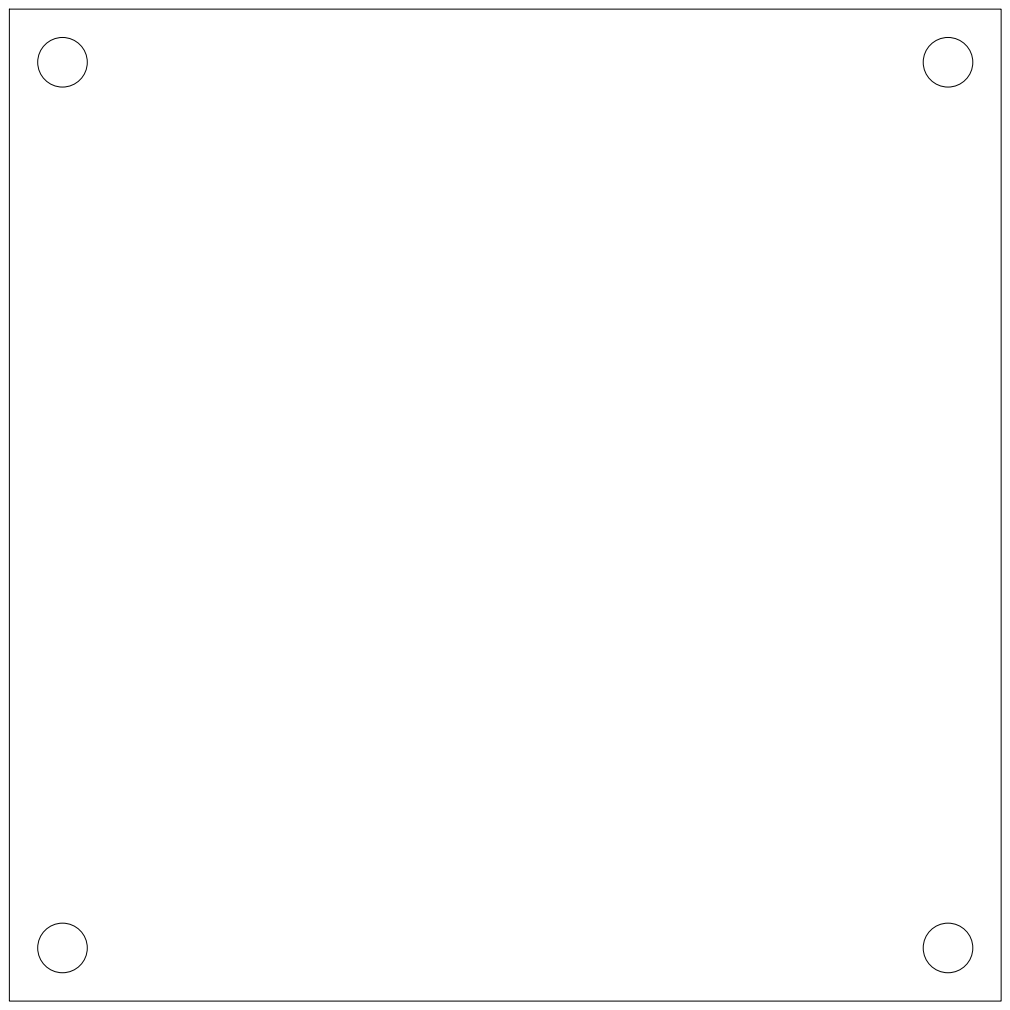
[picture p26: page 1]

Id: 11/11 Title: Spiro Brick

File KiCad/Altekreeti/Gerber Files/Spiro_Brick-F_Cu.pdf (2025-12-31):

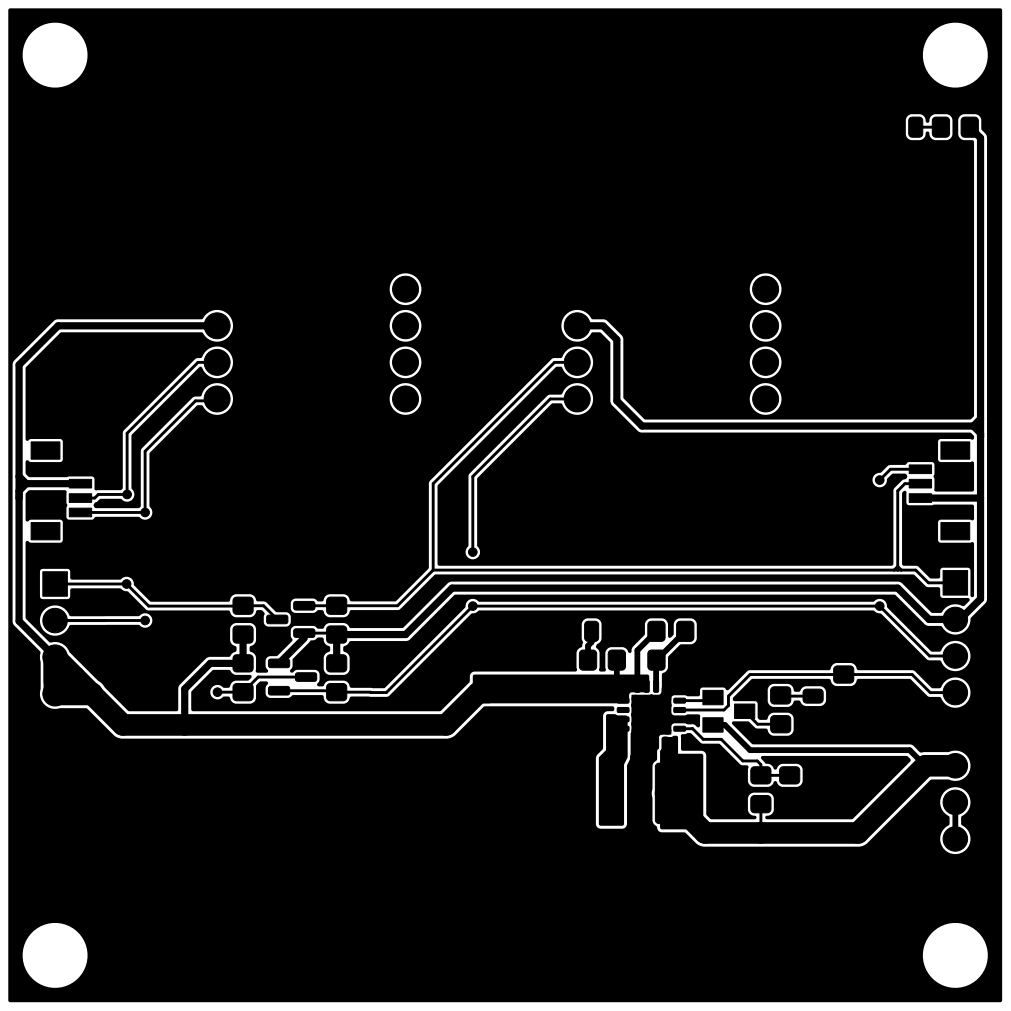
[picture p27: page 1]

Id: 1/11 Title: Spiro Brick

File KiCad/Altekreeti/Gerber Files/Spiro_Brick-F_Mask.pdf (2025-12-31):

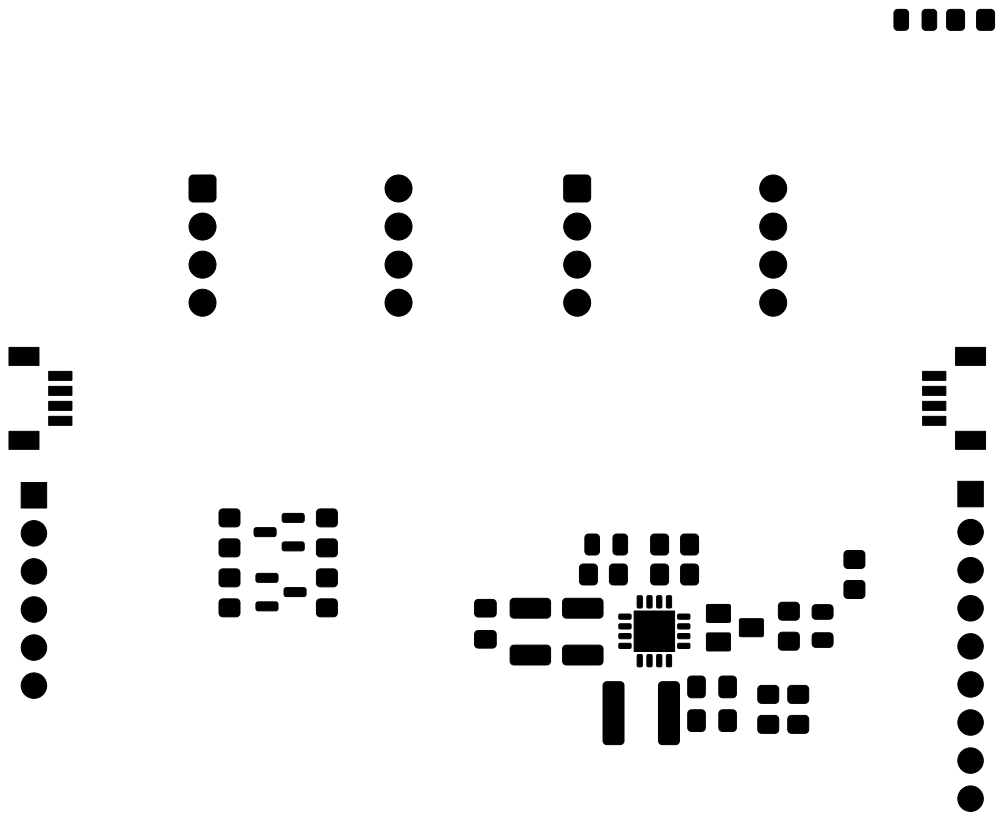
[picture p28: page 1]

Id: 7/11 Title: Spiro Brick

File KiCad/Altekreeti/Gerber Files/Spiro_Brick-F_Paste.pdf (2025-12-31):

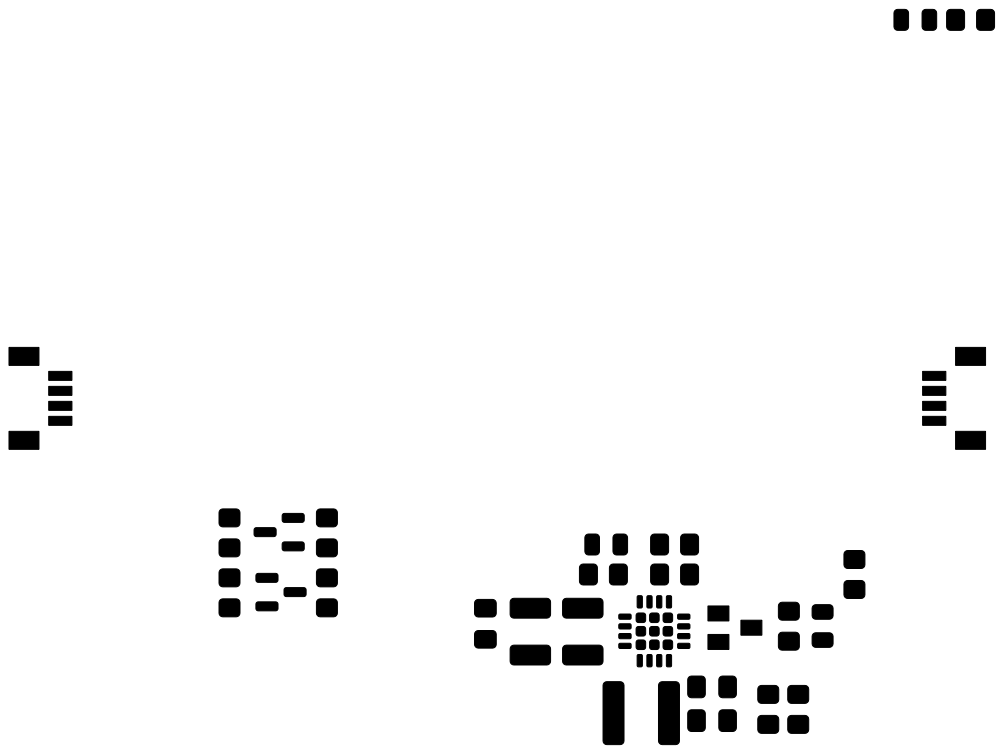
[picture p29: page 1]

Id: 3/11 Title: Spiro Brick

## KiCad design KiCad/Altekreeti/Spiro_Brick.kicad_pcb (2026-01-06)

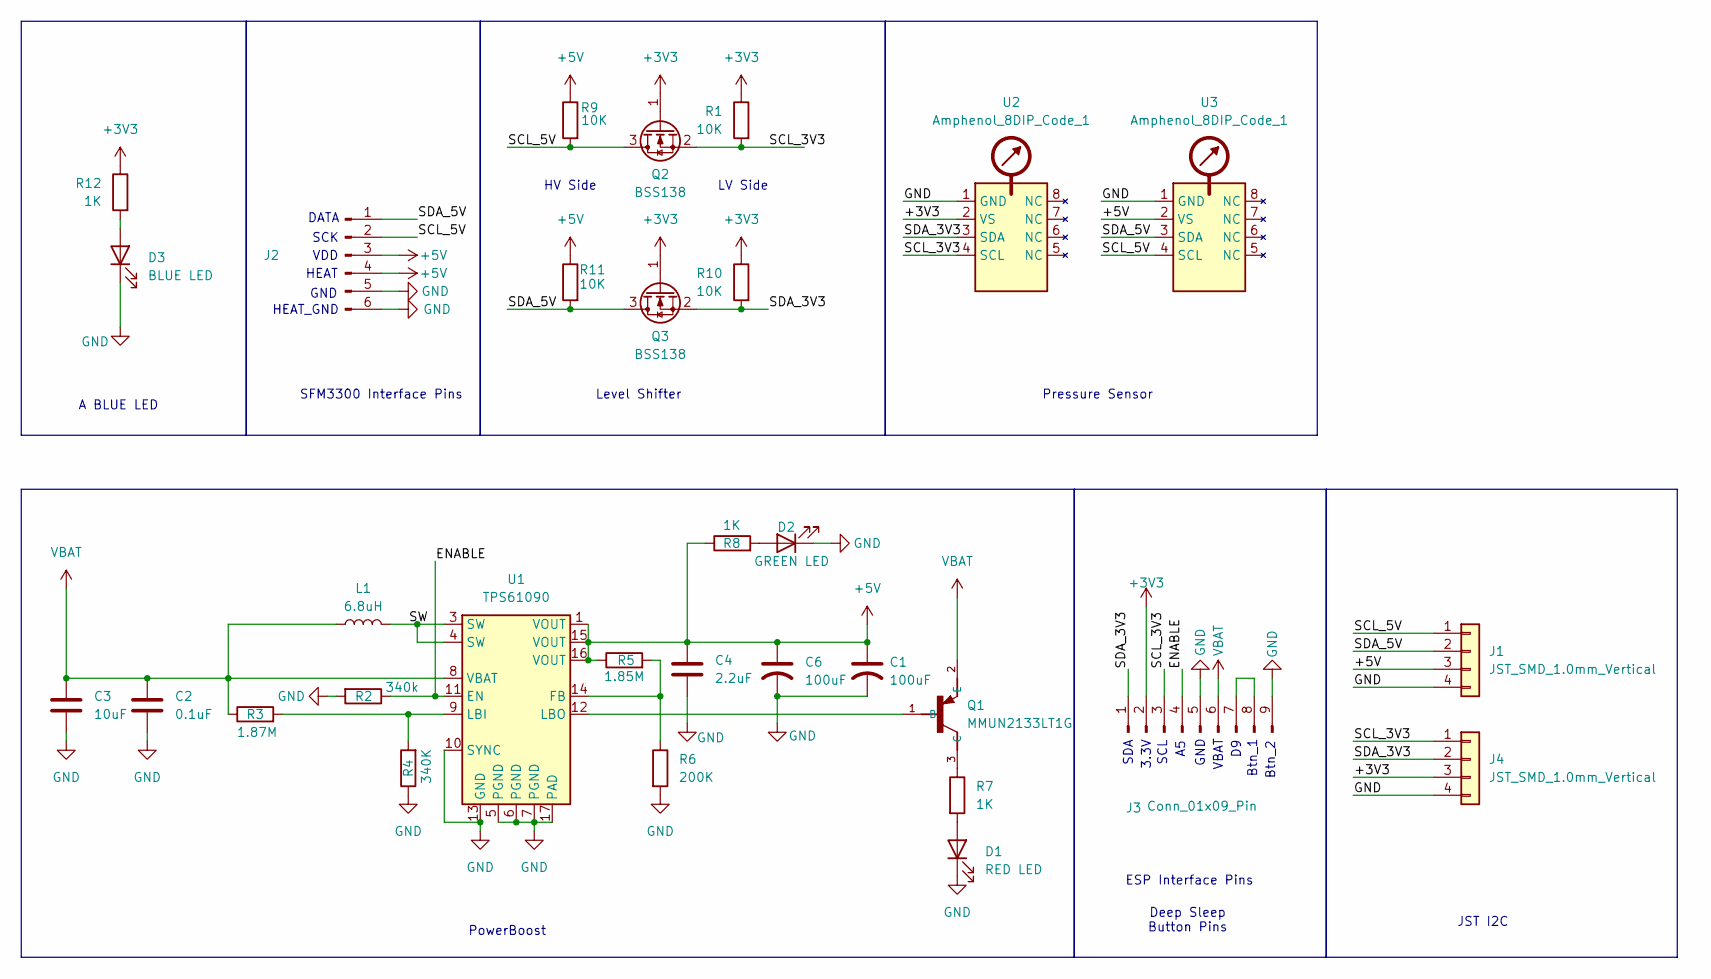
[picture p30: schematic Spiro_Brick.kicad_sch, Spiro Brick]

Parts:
C1, C6: 100uF; C_1210_3225Metric_Pad1.33x2.70mm_HandSolder
C2: 0.1uF; C_0805_2012Metric_Pad1.18x1.45mm_HandSolder
C3: 10uF; C_0805_2012Metric_Pad1.18x1.45mm_HandSolder
C4: 2.2uF; C_0805_2012Metric_Pad1.18x1.45mm_HandSolder
D1: RED LED; LED_0805_2012Metric
D2: GREEN LED; LED_0805_2012Metric
D3: BLUE LED; LED_0805_2012Metric
J1, J4: JST_SMD_1.0mm_Vertical; JST_1x04_P1.0mm_Vertical_SMD
J2: PinHeader_1x06_P2.54mm_Vertical
J3: Conn_01x09_Pin; PinHeader_1x09_P2.54mm_Vertical
L1: 6.8uH; L_Changjiang_FNR5045S
Q1: MMUN2133LT1G; SOT95P240X111-3N
Q2, Q3: BSS138; SOT-23
R1, R9, R10, R11: 10K; R_0805_2012Metric_Pad1.20x1.40mm_HandSolder
R2: 340k; R_0805_2012Metric_Pad1.20x1.40mm_HandSolder
R3: 1.87M; R_0805_2012Metric_Pad1.20x1.40mm_HandSolder
R4: 340K; R_0805_2012Metric_Pad1.20x1.40mm_HandSolder
R5: 1.85M; R_0805_2012Metric_Pad1.20x1.40mm_HandSolder
R6: 200K; R_0805_2012Metric_Pad1.20x1.40mm_HandSolder
R7, R8, R12: 1K; R_0805_2012Metric_Pad1.20x1.40mm_HandSolder
U1: TPS61090; Texas_RSA_VQFN-16-1EP_4x4mm_P0.65mm_EP2.7x2.7mm_ThermalVias
U2, U3: Amphenol_8DIP_Code_1; Amphenol_DIP-8_W13.08mm

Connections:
+3V3: J3.2, J4.3, Q2.1 (G), Q3.1 (G), R1.1, R10.1, R12.1, U2.2 (VS)
+5V: C1.1, C4.1, C6.1, J1.3, J2.3, J2.4, R5.1, R8.1, R9.1, R11.1, U1.1 (VOUT), U1.15 (VOUT), U1.16 (VOUT), U3.2 (VS)
/ENABLE: J3.4, R2.1, U1.11 (EN)
/SCL_3V3: J3.3, J4.1, Q2.2 (S), R1.2, U2.4 (SCL)
/SCL_5V: J1.1, J2.2, Q2.3 (D), R9.2, U3.4 (SCL)
/SDA_3V3: J3.1, J4.2, Q3.2 (S), R10.2, U2.3 (SDA)
/SDA_5V: J1.2, J2.1, Q3.3 (D), R11.2, U3.3 (SDA)
/SW: L1.2, U1.3 (SW), U1.4 (SW)
GND: C1.2, C2.2, C3.2, C4.2, C6.2, D1.1 (K), D2.1 (K), D3.1 (K), J1.4, J2.5, J2.6, J3.5, J3.9, J4.4, R2.2, R4.1, R6.2, U1.5 (PGND), U1.6 (PGND), U1.7 (PGND), U1.10 (SYNC), U1.13 (GND), U1.17 (PAD), U2.1 (GND), U3.1 (GND)
unnamed: D1.2 (A), R7.2
unnamed: D2.2 (A), R8.2
unnamed: D3.2 (A), R12.2
unnamed: J3.7, J3.8
unnamed: Q1.1 (B), U1.12 (LBO)
unnamed: Q1.3 (C), R7.1
unnamed: R5.2, R6.1, U1.14 (FB)
unnamed: R3.2, R4.2, U1.9 (LBI)
VBAT: C2.1, C3.1, J3.6, L1.1, Q1.2 (E), R3.1, U1.8 (VBAT)

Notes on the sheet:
HEAT
SDA
ESP Interface Pins
SFM3300 Interface Pins
Level Shifter
SCK
SCL
HV Side
Deep Sleep Button Pins
Btn_1
Btn_2
LV Side
DATA
Pressure Sensor
GND
VBAT
PowerBoost
A BLUE LED
3.3V
VDD
JST I2C
HEAT_GND

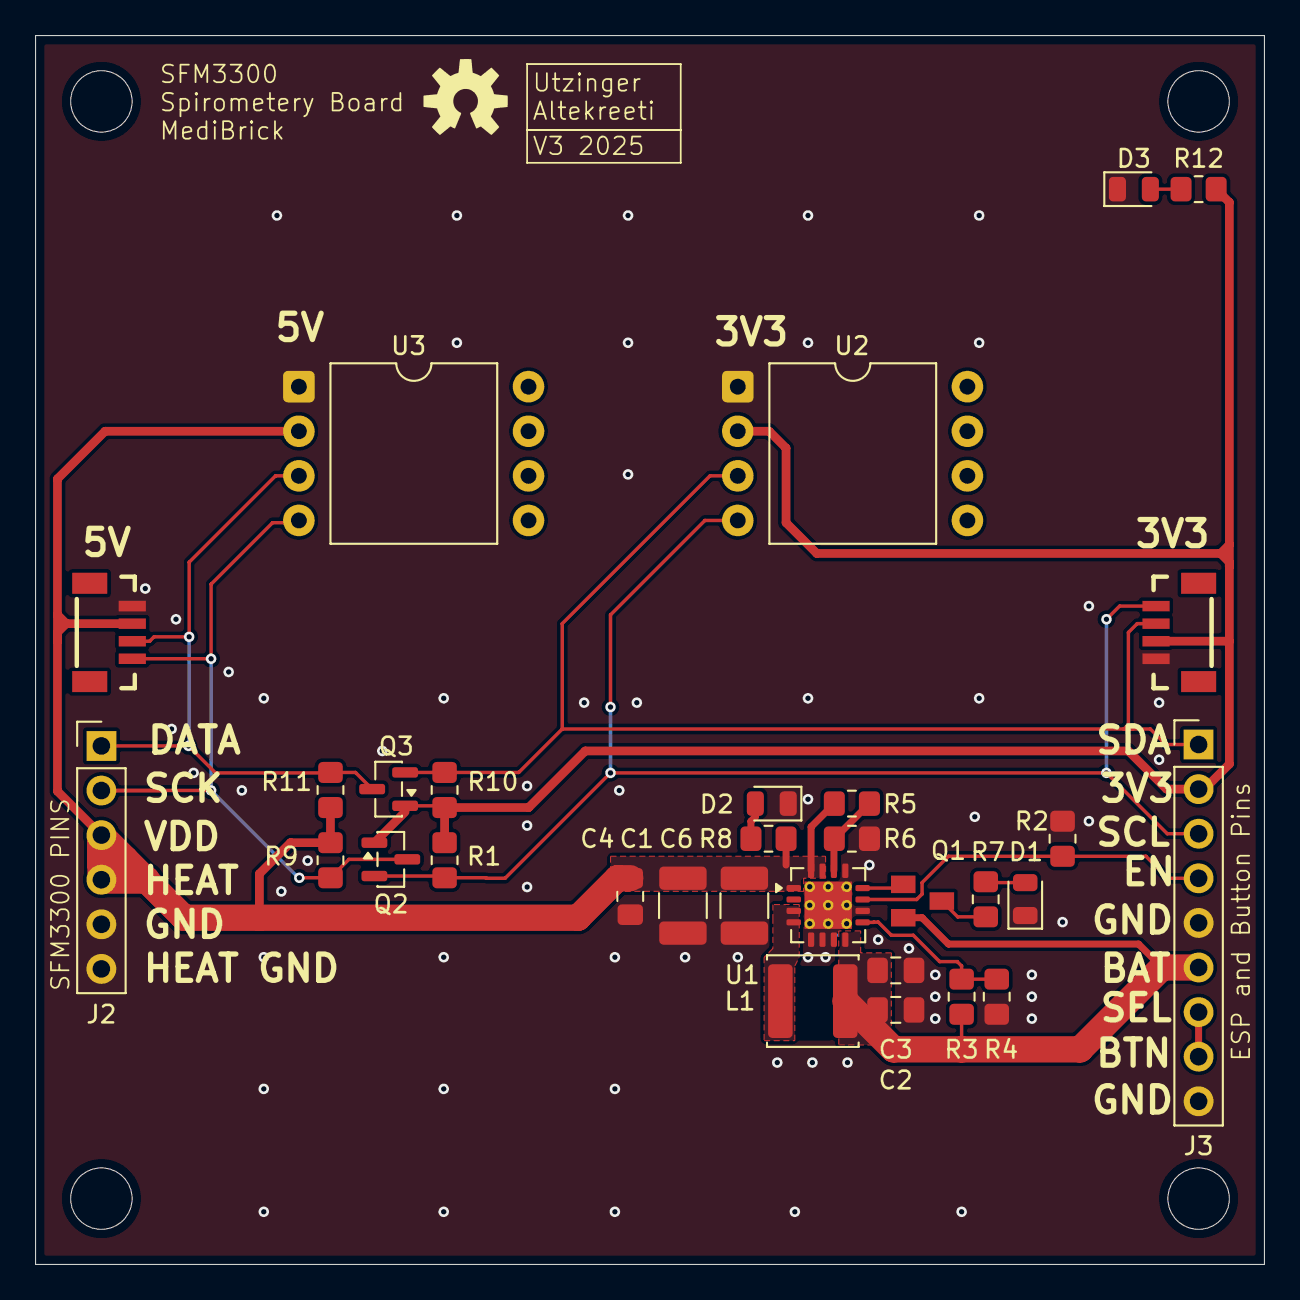
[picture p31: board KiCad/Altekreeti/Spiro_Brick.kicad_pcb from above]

Board: 2 copper layers, 70.0 x 70.0 mm, 31 parts (0 on the bottom side), 18 nets.

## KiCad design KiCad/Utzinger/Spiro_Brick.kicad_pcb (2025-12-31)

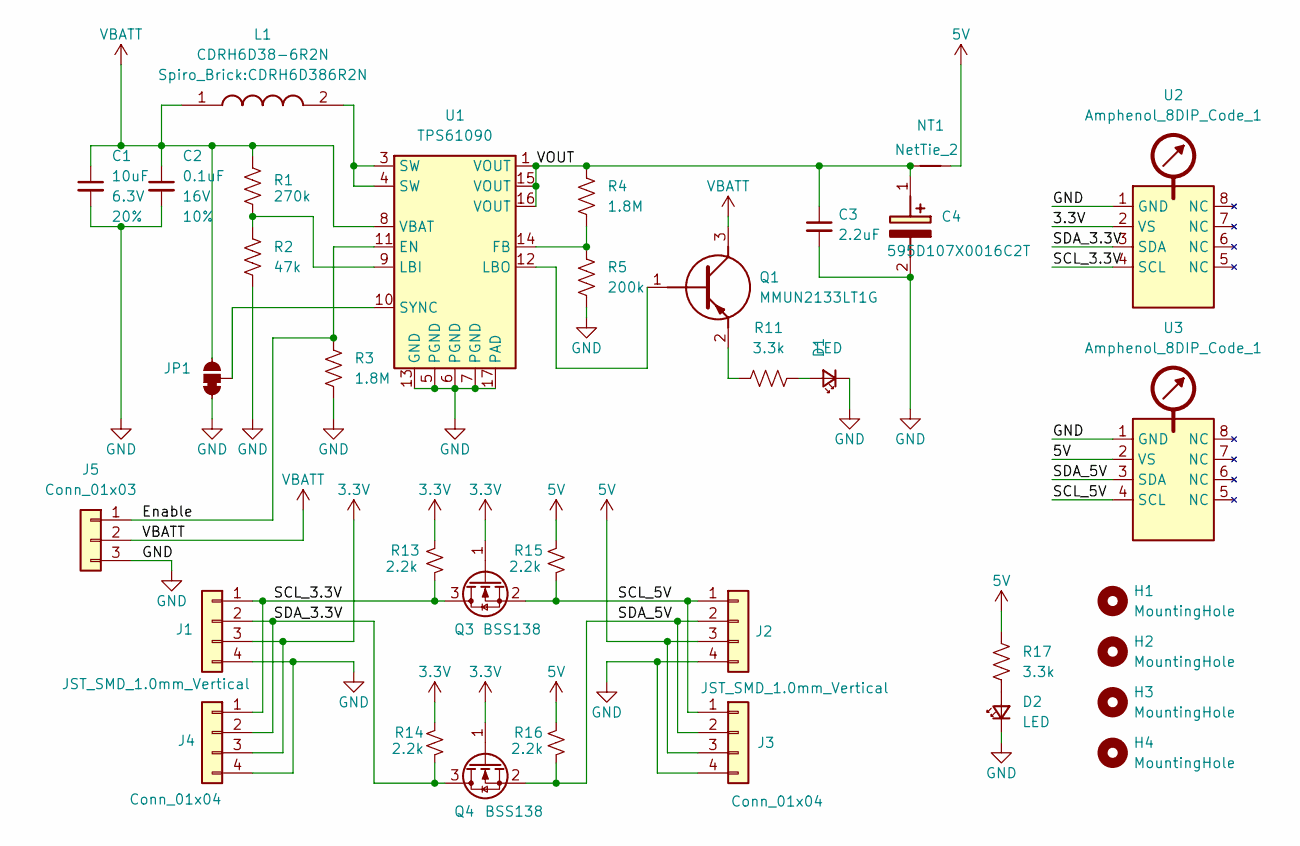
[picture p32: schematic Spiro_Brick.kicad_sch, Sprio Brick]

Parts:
C1: 10uF; C_0402_1005Metric; Voltage 6.3V; Tolerance 20%
C2: 0.1uF; C_0402_1005Metric; Voltage 16V; Tolerance 10%
C3: 2.2uF; C_0402_1005Metric; Voltage 10V; Tolerance 10%
C4: 595D107X0016C2T; CAPPC5932X280N; Manufacturer_Part_Number 595D107X0016C2T; Mouser Part Number 74-595D107X0016C2T
D1, D2: LED; LED_0402_1005Metric
H1, H2, H3, H4: MountingHole; MountingHole_3.2mm_M3
J1, J2: JST_SMD_1.0mm_Vertical; JST_1x04_P1.0mm_Vertical_SMD
J3, J4: Conn_01x04; PinHeader_1x04_P2.54mm_Vertical
J5: Conn_01x03; PinHeader_1x03_P2.54mm_Vertical
JP1: SolderJumper-3_P1.3mm_Bridged12_Pad1.0x1.5mm
L1: CDRH6D38-6R2N; CDRH6D386R2N; Manufacturer_Part_Number CDRH6D38-6R2N
NT1: NetTie_2; NetTie-2_SMD_Pad2.0mm
Q1: MMUN2133LT1G; SOT96P237X111-3N; Manufacturer_Part_Number MMUN2133LT1G; Mouser Part Number 863-MMUN2133LT1G
Q3, Q4: BSS138; SOT-23
R1: 270k; R_0402_1005Metric
R2: 47k; R_0402_1005Metric
R3, R4: 1.8M; R_0402_1005Metric
R5: 200k; R_0402_1005Metric
R11, R17: 3.3k; R_0402_1005Metric
R13, R14, R15, R16: 2.2k; R_0402_1005Metric
U1: TPS61090; Texas_RSA_VQFN-16-1EP_4x4mm_P0.65mm_EP2.7x2.7mm_ThermalVias
U2, U3: Amphenol_8DIP_Code_1; Amphenol_DIP-8_W13.08mm

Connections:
3.3V: J1.3, J4.3, Q3.1 (G), Q4.1 (G), R13.2, R14.2, U2.2 (VS)
5V: J2.3, J3.3, NT1.2, R15.2, R16.2, R17.1, U3.2 (VS)
/Enable: J5.1, R3.1, U1.11 (EN)
/SCL_3.3V: J1.1, J4.1, Q3.3 (D), R13.1, U2.4 (SCL)
/SCL_5V: J2.1, J3.1, Q3.2 (S), R15.1, U3.4 (SCL)
/SDA_3.3V: J1.2, J4.2, Q4.3 (D), R14.1, U2.3 (SDA)
/SDA_5V: J2.2, J3.2, Q4.2 (S), R16.1, U3.3 (SDA)
/VOUT: C3.1, C4.1 (+), NT1.1, R4.1, U1.1 (VOUT), U1.15 (VOUT), U1.16 (VOUT)
GND: C1.2, C2.2, C3.2, C4.2 (-), D1.1 (K), D2.1 (K), J1.4, J2.4, J3.4, J4.4, J5.3, JP1.1 (A), R2.2, R3.2, R5.2, U1.5 (PGND), U1.6 (PGND), U1.7 (PGND), U1.13 (GND), U1.17 (PAD), U2.1 (GND), U3.1 (GND)
unnamed: D1.2 (A), R11.2
unnamed: D2.2 (A), R17.2
unnamed: JP1.2 (B), U1.10 (SYNC)
unnamed: L1.2, U1.3 (SW), U1.4 (SW)
unnamed: Q1.1 (B), U1.12 (LBO)
unnamed: Q1.2 (E), R11.1
unnamed: R4.2, R5.1, U1.14 (FB)
unnamed: R1.2, R2.1, U1.9 (LBI)
VBATT: C1.1, C2.1, J5.2, JP1.3 (C), L1.1, Q1.3 (C), R1.1, U1.8 (VBAT)

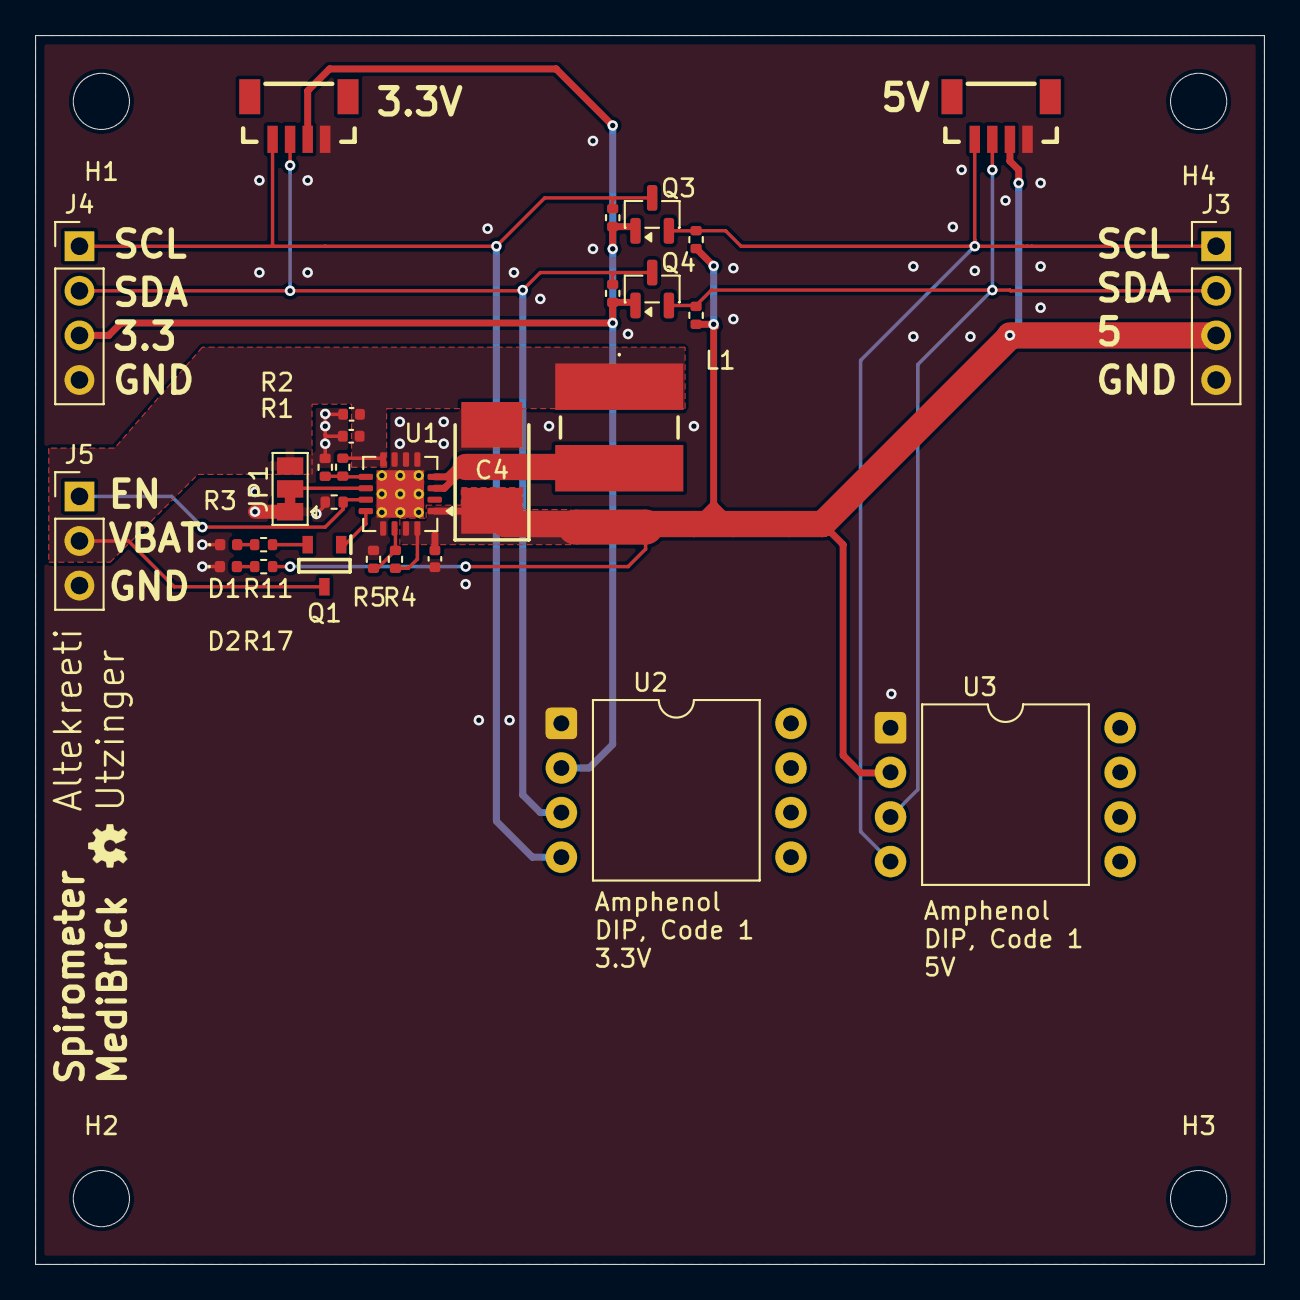
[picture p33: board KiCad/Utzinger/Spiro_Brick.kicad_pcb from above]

Board: 2 copper layers, 70.0 x 70.0 mm, 36 parts (0 on the bottom side), 18 nets.

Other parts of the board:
Ref**: Val**; OSHW_Logo_2.5mm

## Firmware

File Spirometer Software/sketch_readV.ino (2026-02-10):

#include <Arduino.h>
#include <Wire.h>

#include "Adafruit_MAX1704X.h"
#include <Adafruit_GFX.h>
#include <Adafruit_SSD1306.h>

#include <SensirionI2CSfm3000.h>
#include "esp_sleep.h"
#include "driver/rtc_io.h"
#include <math.h>

// ---------- Pins ----------
#define BOOST_EN_PIN A5          // PowerBoost EN (HIGH = ON, LOW = OFF)
#define BTN_PIN      GPIO_NUM_9  // Deep-sleep button: D9 to GND (active LOW)
#define LED_PIN      8           // Your existing PWM pin

// ---------- Display ----------
#define SCREEN_WIDTH 128
#define SCREEN_HEIGHT 32
#define OLED_RESET   -1
#define OLED_ADDR    0x3C
Adafruit_SSD1306 display(SCREEN_WIDTH, SCREEN_HEIGHT, &Wire, OLED_RESET);

// ---------- Battery ----------
Adafruit_MAX17048 maxlipo;
float battV  = NAN;
float battPct = NAN;

// ---------- SFM3300-D ----------
SensirionI2CSfm3000 sfm;
float scalingFactor = 120.0f;
float offset        = 32768.0f;

// ---------- Timing ----------
uint32_t lastBattMS = 0, lastOledMS = 0, lastFlowMS = 0;
const uint32_t BATT_PERIOD_MS = 500;
const uint32_t OLED_PERIOD_MS = 150;

// ---------- Volume integration ----------
float flow    = 0.0f;
float inhaleVol_L = 0.0f;
float exhaleVol_L = 0.0f;

// thresholds
const float flowThreshold  = 0.1f;   // for integration
const float START_THR_SLM  = 0.5f;   // |flow| above this = breath start
const float STOP_THR_SLM   = 0.3f;   // |flow| below this = possible end
const uint32_t STOP_TIME_MS = 800;   // must stay low this long to end breath

// Breath state machine
enum BreathState {
  BREATH_WAIT_START,
  BREATH_MEASURING,
  BREATH_HOLD
};

BreathState breathState     = BREATH_WAIT_START;
BreathState lastBreathState = BREATH_WAIT_START;
uint32_t quietStartMS       = 0;

// NEW: Inhale / exhale phase for continuous monitoring
enum Phase { PHASE_NONE, PHASE_INHALE, PHASE_EXHALE };
Phase currentPhase = PHASE_NONE;

// Tidal-volume display timing
uint32_t holdDisplayStartMS = 0;
bool     holdDisplayActive  = false;

// ---------- Helpers ----------
void drawBatteryBar(float percent) {
  int x=0, y=18, w=128, h=10;
  percent = constrain(percent, 0.0f, 100.0f);
  int fillW = (int)(w * (percent/100.0f));
  display.drawRect(x, y, w, h, SSD1306_WHITE);
  display.fillRect(x+1, y+1, max(0, fillW-2), h-2, SSD1306_WHITE);
}

// Battery + flow screen (WAIT_START / idle)
void showBatteryScreen(float flow_slm) {
  display.clearDisplay();
  display.setTextColor(SSD1306_WHITE);
  display.setTextSize(1);
  display.setCursor(0,0);

  display.print(F("Batt "));
  if (isnan(battPct)) display.print(F("--.-% "));
  else { display.print(battPct,1); display.print('%'); display.print(' '); }
  if (isnan(battV)) display.print(F("--.--V"));
  else { display.print(battV,2); display.print('V'); }

  drawBatteryBar(isnan(battPct) ? 0.0f : battPct);

  display.setCursor(0, 30-8);
  display.print(F("Flow "));
  display.print(flow_slm, 2);
  display.print(F(" slm"));
  display.display();
}

// Live inhale / exhale screen during MEASURING
void showInhaleExhaleScreen(float inh_L, float exh_L) {
  display.clearDisplay();
  display.setTextColor(SSD1306_WHITE);
  display.setTextSize(1);

  display.setCursor(0, 0);
  display.print(F("INH: "));
  display.print(inh_L, 2);
  display.println(F(" L"));

  display.setCursor(0, 16);
  display.print(F("EXH: "));
  display.print(exh_L, 2);
  display.println(F(" L"));

  display.display();
}

// Tidal volume result screen during HOLD
void showTidalScreen(float tidal_L) {
  display.clearDisplay();
  display.setTextColor(SSD1306_WHITE);

  display.setTextSize(1);
  display.setCursor(0, 0);
  display.println(F("Tidal Volume"));

  display.setTextSize(2);
  display.setCursor(0, 15);
  display.print(tidal_L, 2);
  display.print(F(" L"));

  display.display();
}

void setup() {
  pinMode(LED_PIN, OUTPUT);
  analogWrite(LED_PIN, 255);          // your existing LED behavior

  Serial.begin(115200);
  while (!Serial) { delay(100); }

  // ---- Boost EN ----
  pinMode(BOOST_EN_PIN, OUTPUT);
  digitalWrite(BOOST_EN_PIN, HIGH);   // turn Boost ON while code is running

  // ---- I2C / OLED ----
  Wire.begin();
  if (!display.begin(SSD1306_SWITCHCAPVCC, OLED_ADDR)) {
    Serial.println(F("SSD1306 allocation failed"));
    for(;;);
  }
  display.clearDisplay();
  display.setTextColor(SSD1306_WHITE);
  display.setTextSize(1);
  display.setCursor(0,12);
  display.println(F("Battery Level:"));
  display.setCursor(0,28);
  display.print(F("--%"));
  display.display();
  delay(1500);

  // ---- Fuel Gauge ----
  maxlipo.begin();

  // ---- Flow sensor ----
  uint16_t error;
  char errorMessage[64];

  sfm.begin(Wire, SFM300_I2C_ADDRESS_0);

  uint32_t serialNumber;
  error = sfm.readSerialNumber(serialNumber);
  if (error) {
    Serial.print("Error serialNumber(): ");
    errorToString(error, errorMessage, 64);
    Serial.println(errorMessage);
  } else {
    Serial.print("SerialNumber: ");
    Serial.println(serialNumber);
  }

  error = sfm.startContinuousMeasurement();
  if (error) {
    Serial.print("Error startContinuousMeasurement(): ");
    errorToString(error, errorMessage, 64);
    Serial.println(errorMessage);
  }

  // ---- Button / deep sleep ----
  pinMode((int)BTN_PIN, INPUT_PULLUP);

  rtc_gpio_init(BTN_PIN);
  rtc_gpio_set_direction(BTN_PIN, RTC_GPIO_MODE_INPUT_ONLY);
  rtc_gpio_pullup_en(BTN_PIN);
  rtc_gpio_pulldown_dis(BTN_PIN);

  esp_sleep_enable_ext0_wakeup(BTN_PIN, 0);   // wake on LOW
  esp_sleep_pd_config(ESP_PD_DOMAIN_RTC_PERIPH, ESP_PD_OPTION_ON);

  // Welcome if we woke from deep sleep
  esp_sleep_wakeup_cause_t cause = esp_sleep_get_wakeup_cause();
  if (cause == ESP_SLEEP_WAKEUP_EXT0) {
    display.clearDisplay();
    display.setCursor(0, 0);
    display.println(F("Welcome"));
    display.display();
    delay(1200);
  }

  lastFlowMS = millis();
  breathState = BREATH_WAIT_START;
  lastBreathState = BREATH_WAIT_START;
  inhaleVol_L = exhaleVol_L = 0.0f;
  currentPhase = PHASE_NONE;
  holdDisplayActive = false;
}

void loop() {
  uint16_t error;
  char errorMessage[64];
  uint32_t now = millis();

  // ---- Read flow ----
  float flow_slm = 0.0f;
  error = sfm.readMeasurement(flow, scalingFactor, offset);
  if (!error) {
    flow_slm = flow; // SLM (L/min)
  } else {
    Serial.print("readMeasurement error: ");
    errorToString(error, errorMessage, 64);
    Serial.println(errorMessage);
  }

  float dt = (now - lastFlowMS) / 1000.0f;  // seconds
  if (dt < 0) dt = 0;
  lastFlowMS = now;

  float absFlow = fabs(flow_slm);

  // ---- Breath state transitions ----
  if (breathState == BREATH_HOLD && lastBreathState != BREATH_HOLD) {
    // Just entered HOLD: start showing tidal volume for this last cycle
    holdDisplayActive  = true;
    holdDisplayStartMS = now;
  }
  lastBreathState = breathState;

  switch (breathState) {
    case BREATH_WAIT_START:
      // Reset everything while idle
      inhaleVol_L  = 0.0f;
      exhaleVol_L  = 0.0f;
      currentPhase = PHASE_NONE;
      quietStartMS = 0;

      if (absFlow > START_THR_SLM) {
        breathState = BREATH_MEASURING;
        Serial.println(F("Breath started"));
      }
      break;

    case BREATH_MEASURING:
      // ---- Continuous monitoring: each inhale/exhale cycle independent ----
      if (flow_slm > flowThreshold) {
        // New exhale cycle starts
        if (currentPhase != PHASE_EXHALE) {
          exhaleVol_L  = 0.0f;       // reset exhale for this cycle
          currentPhase = PHASE_EXHALE;
        }
        float Lps = flow_slm / 60.0f; // L/min -> L/s
        exhaleVol_L += Lps * dt;

      } else if (flow_slm < -flowThreshold) {
        // New inhale cycle starts
        if (currentPhase != PHASE_INHALE) {
          inhaleVol_L  = 0.0f;       // reset inhale for this cycle
          currentPhase = PHASE_INHALE;
        }
        float Lps = (-flow_slm) / 60.0f;
        inhaleVol_L += Lps * dt;

      } else {
        // Near zero -> no active phase
        currentPhase = PHASE_NONE;
      }

      // Check for breath end (flow near zero long enough)
      if (absFlow < STOP_THR_SLM) {
        if (quietStartMS == 0) {
          quietStartMS = now;
        } else if ((now - quietStartMS) >= STOP_TIME_MS) {
          breathState = BREATH_HOLD;
          currentPhase = PHASE_NONE;
          Serial.println(F("Breath finished, volumes held"));
        }
      } else {
        quietStartMS = 0;
      }
      break;

    case BREATH_HOLD:
      // Do not integrate; volumes stay fixed
      break;
  }

  // ---- Serial debug ----
  Serial.print("Flow = ");
  Serial.print(flow_slm, 2);
  Serial.print(" SLM, INH = ");
  Serial.print(inhaleVol_L, 3);
  Serial.print(" L, EXH = ");
  Serial.print(exhaleVol_L, 3);
  Serial.print(" L, State = ");
  if (breathState == BREATH_WAIT_START) Serial.println("WAIT_START");
  else if (breathState == BREATH_MEASURING) Serial.println("MEASURING");
  else Serial.println("HOLD");

  // ---- Battery update ----
  if (now - lastBattMS >= BATT_PERIOD_MS) {
    lastBattMS = now;
    float v = maxlipo.cellVoltage();
    if (!isnan(v)) {
      battV   = v;
      battPct = maxlipo.cellPercent();
    }
  }

  // ---- OLED update ----
  if (now - lastOledMS >= OLED_PERIOD_MS) {
    lastOledMS = now;

    bool showTidal  = false;
    bool showInhExh = false;

    // Tidal volume window
    if (breathState == BREATH_HOLD && holdDisplayActive) {
      if ((now - holdDisplayStartMS) <= 20000UL) {      // 20 seconds
        showTidal = true;
      } else {
        // 20 s finished → go back to WAIT_START for next breath
        holdDisplayActive = false;
        breathState = BREATH_WAIT_START;
        inhaleVol_L = exhaleVol_L = 0.0f;
        currentPhase = PHASE_NONE;
      }
    }

    // During active breath, show live INH / EXH
    if (breathState == BREATH_MEASURING) {
      showInhExh = true;
    }

    if (showTidal) {
      float tidal_L = max(inhaleVol_L, exhaleVol_L);    // last cycle’s volume
      showTidalScreen(tidal_L);
    } else if (showInhExh) {
      showInhaleExhaleScreen(inhaleVol_L, exhaleVol_L);
    } else {
      // Idle / between breaths
      showBatteryScreen(flow_slm);
    }
  }

  // ---- Deep-sleep button ----
  int btnLevel = digitalRead((int)BTN_PIN);   // LOW when pressed
  if (btnLevel == LOW) {
    delay(40);
    if (digitalRead((int)BTN_PIN) == LOW) {
      display.clearDisplay();
      display.setCursor(0, 0);
      display.println(F("Going to"));
      display.println(F("deep sleep..."));
      display.display();

      delay(5000); // 5 s grace

      // Turn OLED OFF & Boost OFF for low power
      display.ssd1306_command(SSD1306_DISPLAYOFF);
      digitalWrite(BOOST_EN_PIN, LOW);

      Serial.flush();
      esp_deep_sleep_start(); // never returns until wake
    }
  }

  delay(50);   // ~20 Hz loop
}

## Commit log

2026-01-06 Fix inductor ground loop
    [BOM spirometer V3-1.xlsx, Spiro_Brick-B_Cu.gbr, Spiro_Brick-B_Mask.gbr, Spiro_Brick-B_Paste.gbr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]
2026-05-06 Add Faceplate Assembly
